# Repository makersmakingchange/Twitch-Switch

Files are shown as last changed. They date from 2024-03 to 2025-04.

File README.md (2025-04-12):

<!---  Open Source Assistive Technology: GitHub Readme Template Version 1.1 (2024-Mar-15)  --->

<!--- INSTRUCTIONS This is a markdown template for creating the README.md file in a GitHub repository. This file is rendered and displayed automatically when someone visits the repository.  --->  
 
 <!---  TITLE Should match the name of the GitHub repository. Choose something descriptive rather than whimsical.   --->
# Twitch Switch

<!---  SUMMARY A brief summary of the project. What it does, who it is for, how much it costs.  --->
The Twitch Switch is for users with limited movement capabilities. Up to three small wireless sensors can capture very small movements. The Twitch Switch can be used for activating up to three switch adapted devices or emulating a mouse or keyboard to operate a digital device such as a computer. 

The Twitch Switch works best for someone who is only able to perform small movements. There are three sensors that can be placed wherever the user has the most controlled, repeatable, intentional movement. Sensor placement can include on the user's finger, wrist, foot, or head. The sensors are powered by rechargeable batteries and connect wirelessly to a controller. The sensitivity of each sensor can be adjusted using knobs on the controller.

The first way to use the Twitch Switch allows the user to activate up to 3 switch adapted devices. Whenever the corresponding switch is moved (even slightly!), the switch adapted device will be activated. 
The second way to use the Twitch Switch is for controlling a digital device such as a computer, tablet, or smartphone. The Twitch Switch can connect via Bluetooth or USB, and has 3 modes: mouse mode, tablet mode, and keyboard mode (which is best for switch control).

The Twitch Switch is intended primarily for people who have some controlled, repeatable, intentional movement, but otherwise have limited mobility and/or dexterity. This device may be beneficial for users with cerebral palsy (CP), spinal cord injuries (SCI), amyotrophic lateral sclerosis (ALS), muscular dystrophy (MD), locked-in syndrome (LIS), traumatic brain injury (TBI), or other disabilities or conditions that significantly limit movement.

The total cost of materials to build this device is around \$360 (plus component shipping). The cost of materials per unit is around \$200 (plus component shipping) if you are able to build in bulk.

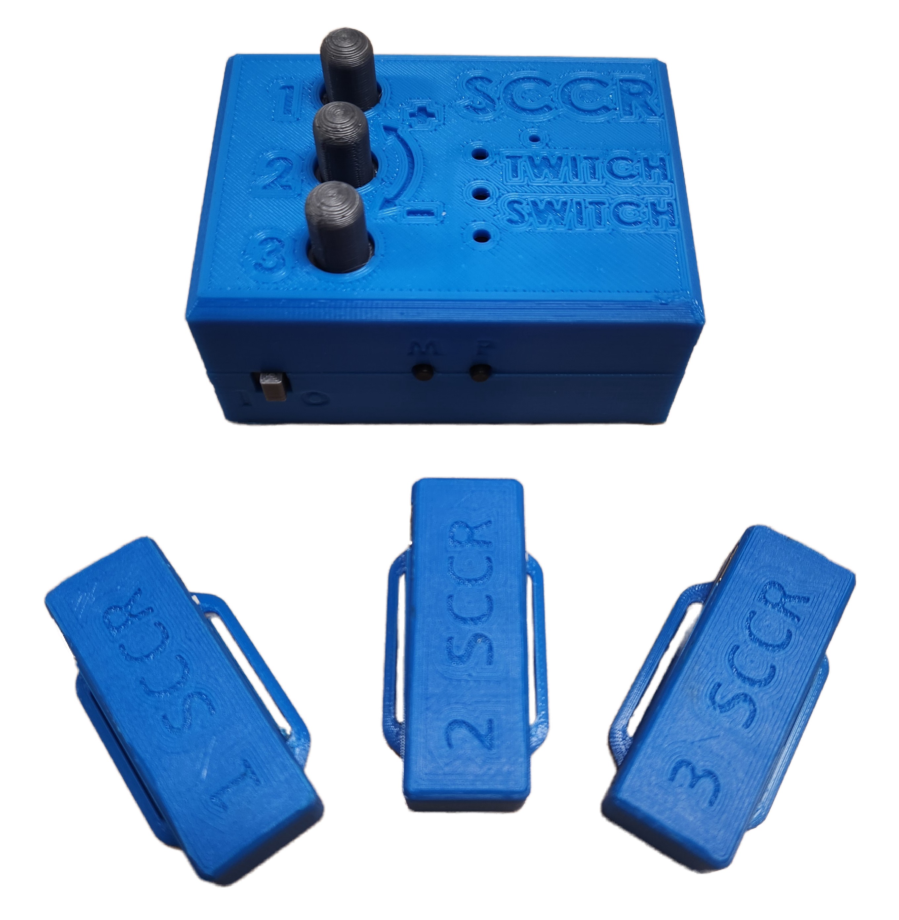
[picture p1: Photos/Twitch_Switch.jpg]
Picture of a Twitch Switch with the controller and three wearable sensors.


## More info at
- [Makers Making Change Assistive Device Library Listing](https://www.makersmakingchange.com/s/product/twitch-switch/01tJR000003UiebYAC)

## How to Obtain the Device
### 1. Do-it-Yourself (DIY) or Do-it-Together (DIT)

This is an open-source assistive technology, so anyone is free to build it. All of the files and instructions required to build the device are contained within this repository. Refer to the Maker Guide below.

### 2. Request a build of this device

You may also submit a build request through the [Makers Making Change Assistive Device Listing](https://www.makersmakingchange.com/s/product/twitch-switch/01tJR000003UiebYAC) to have a volunteer maker build the device. As the requestor, you are responsible for reimbursing the maker for the cost of materials and any shipping.

### 3. Build this device for someone else

If you have the skills and equipment to build this device, and would like to donate your time to create the device for someone who needs it, visit the [MMC Maker Wanted](https://makersmakingchange.com/maker-wanted/) section.

## Build Instructions

### 1. Read through the Maker Guide

The [Maker Guide](/Documentation/Twitch_Switch_Maker_Guide.pdf) contains all the necessary information to build this device, including tool lists, assembly instructions, programming instructions and testing.

### 2. Order the Custom PCBs

This build requires two customs PCBS: one custom PCB for the controller and one custom PCB for each of the three sensors. The sensor PCB has a number of surface mount components and it is recommended to have the PCB fabricator assemble these components on the board.

### 3. Order the Off-The-Shelf Components

The [Bill of Materials](/Documentation/Twitch_Switch_BOM.csv) lists all of the parts and components required to build the device.

### 4. Print the 3D Printable components

All of the files and individual print files can be in the [/Build_Files/3D_Printing_Files](/Build_Files/3D_Printing_Files/) folder. Instructions and settings are provided in the 3D Printing Guide section of the [Maker Guide](/Documentation/Twitch_Switch_Maker_Guide.pdf).

### 5. Assemble the Twitch Switch

Reference the [Maker Guide](/Documentation/Twitch_Switch_Maker_Guide.pdf) for the tools and steps required to build each portion.

## How to improve this Device
As open source assistive technology, you are welcomed and encouraged to improve upon the design. 

## Files
### Documentation
| Document             | Version | Link |
|----------------------|---------|------|
| Maker Guide          | 1.0     | [Twitch Switch_Maker_Guide](/Documentation/Twitch_Switch_Maker_Guide.pdf)     |
| Bill of Materials    | 1.0     | [Twitch Switch_Bill_of_Materials](/Documentation/Twitch_Switch_BOM.csv)     |
| User Guide           | 1.0     | [Twitch Switch_User_Guide](/Documentation/Twitch_Switch_User_Guide.pdf)    |
| Changelog            | 1.0     | [Changelog](CHANGES.txt)     |

### Design Files
<!--- DESIGN FILES Include a copy of the original design files to facilitate easy editing and customization. Consider also including a generic format (e.g., STEP) --->
 - [CAD Files](/Design_Files/CAD_Design_Files)
 - [PCB Files](/Design_Files/PCB_Design_Files)

<!--- BUILD FILES Include a copy of the build files intended for manufacturing. This may include svg files for laser cutting, stl files for 3d printing, Gerber files for custom PCBs, and Arduino files for custom firmware --->
### Build Files
 - [3D Printing Files](/Build_Files/3D_Printing_Files)
 - [PCB Build Files](/Build_Files/PCB_Build_Files)
 - [Firmware Files](/Build_Files/Firmware_Files)

<!--- ATTRIBUTION Provide any necessary attribution for designs or components that are included in the device or as part of the project. --->
## Attribution

The Twitch Switch was designed by the Rehabilitation Engineering Department at Horizon Health's, Stan Cassidy Centre for Rehabilitation (SCCR).  Development was supported through the Government of Canada's Innovation Science and Economic Development [Accessible Technology Program](https://ised-isde.canada.ca/site/accessible-technology-program). The ATP program enabled SCCR to deploy numerous Twitch Switches to users at reduced cost.

The latest design (V3.0) incorporates feedback and suggestions from numerous users, clinicians, and volunteer makers.

The latest design incorporates several commercially available open source hardware components from [Adafruit](https://www.adafruit.com/). The Twitch Switch firmware utilizes the [Arduino](https://www.arduino.cc/) development platform, and a number of libraries developed and shared by the open source community.

<!---
This is the attribution for the template.
--->
The documentation template was created by Makers Making Change / Neil Squire Society and is used under a CC BY-SA 4.0 license. It is available at the following link: [https://github.com/makersmakingchange/OpenAT-Template](https://github.com/makersmakingchange/OpenAT-Template)

<!--- CONTRIBUTORS List the names of the people that contributed to the design. This could include the original source of the idea, designers, testers, documenters, etc. --->
### Contributors
- Rachelle Bernier, Horizon Health Network. 
- Marla Calder, Horizon Health Network 
- Natasha Hanson, Horizon Health Network 
- Dorian Hawkes, Horizon Health Network 
- Rick McCaskill, Horizon Health Network 
- Billie O'Connor, Horizon Health Network 
- Kristen Culberson, Horizon Health Network 
- Josie Versloot, Neil Squire Society / Makers Making Change
 
<!--- LICENSE Add the year(s) for the copyright and the Designer Name. You may use the standard set of open licenses or choose your own for the hardware, software, and accompanying materials. --->
## License
Copyright (c) 2020-2024 Stan Cassidy Center for Rehabilitation.

This repository describes Open Hardware:
 - Everything needed or used to design, make, test, or prepare the Twitch Switch is licensed under the [CERN 2.0 Weakly Reciprocal license (CERN-OHL-W v2) or later](https://cern.ch/cern-ohl ) .
 - All software is under the [GNU General Public License v3.0 (GPL-3.0)](https://www.gnu.org/licenses/gpl.html).
 - Accompanying material such as instruction manuals, videos, and other copyrightable works that are useful but not necessary to design, make, test, or prepare the Twitch Switch are published under a [Creative Commons Attribution-ShareAlike 4.0 license (CC BY-SA 4.0)](https://creativecommons.org/licenses/by-sa/4.0/) .

You may redistribute and modify this documentation and make products using it under the terms of the [CERN-OHL-W v2](https://cern.ch/cern-ohl).
This documentation is distributed WITHOUT ANY EXPRESS OR IMPLIED WARRANTY, INCLUDING OF MERCHANTABILITY, SATISFACTORY QUALITY AND FITNESS FOR A PARTICULAR PURPOSE.
Please see the CERN-OHL-W v2 for applicable conditions.

Source Location: https://github.com/makersmakingchange/Twitch-Switch

List of open source licenses. Hardware: CERN-OHL-W-2.0, Software: GPL-3.0-or-later, Documentation: CC-BY-SA-4.0.

---

<!-- ABOUT MMC START -->
## About Makers Making Change
[Makers Making Change Logo](https://www.makersmakingchange.com/)

Makers Making Change is a program of [Neil Squire](https://www.neilsquire.ca/), a Canadian non-profit that uses technology, knowledge, and passion to empower people with disabilities.

Makers Making Change leverages the capacity of community based Makers, Disability Professionals and Volunteers to develop and deliver affordable Open Source Assistive Technologies.

 - Website: [www.MakersMakingChange.com](https://www.makersmakingchange.com/)
 - GitHub: [makersmakingchange](https://github.com/makersmakingchange)
 - Bluesky: [@makersmakingchange.bsky.social](https://bsky.app/profile/makersmakingchange.bsky.social)
 - Instagram: [@makersmakingchange](https://www.instagram.com/makersmakingchange)
 - Facebook: [makersmakechange](https://www.facebook.com/makersmakechange)
 - LinkedIn: [Neil Squire Society](https://www.linkedin.com/company/neil-squire-society/)
 - Thingiverse: [makersmakingchange](https://www.thingiverse.com/makersmakingchange/about)
 - Printables: [MakersMakingChange](https://www.printables.com/@MakersMakingChange)

### Contact Us
For technical questions, to get involved, or to share your experience we encourage you to [visit our website](https://www.makersmakingchange.com/) or [contact us](https://www.makersmakingchange.com/s/contact).
<!-- ABOUT MMC END -->

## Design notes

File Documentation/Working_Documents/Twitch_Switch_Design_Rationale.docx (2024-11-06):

# Introduction

# Research

## Commercially Available Options

Title
Link
Author
License
Cost
Notes

## DIY Options

Title
Link
Author
License
Cost
Test Build (Y/N)
Add to Library (Y/N)
Notes

## Research Summary

<Summary of findings; potentially viable solutions; any gaps in existing options>

# Requirements

## Goals

G01
G02
G03

## Functional Requirements

F01
F02
F03

## Non-functional Requirement

NF01
NF02
NF03

## Constraints

C01
C02
C03

# Ideation

## Key Features

# Conceptual Design

# Prototyping

# Testing

# Detailed Design

# MVP Design

# Final Design

Programmer

https://github.com/SpenceKonde/AVR-Guidance/blob/master/UPDI/jtag2updi.md

Required Hardware

There has been some debate and questions have been raised over whether the recommendations below are the best. More study is required.

A USB serial adapter These can be had for as low as $1 on eBay and AliExpress based on the CH340G, slightly more for CP210x or "FT232". Ideally, you want to dedicate a serial adapter to this purpose for ease of use, rather than having to connect and disconnect things every time you want to switch between programming with it and using as a serial adapter

a fast signal Schottky diode such as one of the BAT series (BAT43, BAT54) or any of many others (recommended) or a resistor (see below to figure out value)).

1 resistor, a few hundred ohms - 220 to 1k, even 2k is fine (may not be needed).

A few jumper wires. Plan to replace these periodically if you use it a lot. Cheap dupont terminals don't last. Actual DuPont terminals (now made by Amphenol F. C. I) hold up much better, but they cost a fortune.

# Opportunities for Improvement / Future Work

## Controller

- Slide switch is tricky to solder, consider a through hole option
- Radio is a bit tricky to solder
- Could a 3D printed piece work for the LED spacer instead of the tubing? This would then be one less part to buy, and not have to worry about the precision of the cut on the tubing (slightly crooked causes the LED to be crooked)
- Add chamfers to screw holes to make screws easier to insert
- Consider adding a shadow line/inner ledge to help with alignment while screwing the case together
- 5.5 cm seemed to be a bit too wide for the foam, the PCB didn’t quite lay flat, maybe cut this down to 5.3 or 5 cm
- Covers on the buttons on the side could make them easier to press
- Foam pushes up on PCB, and there is nothing to keep the PCB down on the left side, so the knob buttons are getting jammed by being pressed down by the enclosure
- Consider adding bumps to the knobs to make them easier to turn
- Screws
  - 25 mm M2 Screws are hard to source in small quantities. These could be replaced with shorter sheet metal type screws to fasten the enclosure
  - Screws can be easy to strip

## Sensors

- Same as above, slide switch and radio are tricky to solder
- Consider adding hard stops to the sensor enclosure bottom to prevent the PCB from getting pushed down too far and damaging the slide switch
  - I accidentally pushed mine too far down and the slide switch bent upwards
- Consider adding a switch cover to the slide switch on the sensor to make it easier to turn on and off
- Easier way to program boards that does not require custom programmer
- If using custom programmer, more solid connection

## Lithium Batteries

- Need to be extremely cautious with the polarity of connectors from different suppliers!
- These can pose a safety risk and the user should be warned accordingly.

© 2023 by <Author>. This work is licensed under the CC BY SA 4.0 License: http://creativecommons.org/licenses/by-sa/4.0 Files available at <Replace with MMC Library Link> Page 1 of 1

VX.X | <MONTH> <YEAR> <Device Name> Design Rationale

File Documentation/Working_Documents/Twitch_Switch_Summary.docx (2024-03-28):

This document is intended to be a summary of a device to make it easier to add to the website.

# Product Information

## Product Name

Twitch Switch

## Device Category

| Adapted Toys
| Aids for Daily Living (ADL)
X | Assistive Switches
| Communication Aids (AAC)
X | Computer Access
| Environmental Controls
X | Gaming
| Keyguard
| Kits
| LipSyncs
| Mounting
| Recreation and Leisure
| Seating and Positioning
| Switch Interfaces
| Writing Aids

## User Value Statement

An alternative to assistive switches, the Twitch Switch allows you to activate up to 3 switch adapted devices, or emulate a mouse or keyboard with movement as subtle as twitching your eyebrow.

## Designer

Stan Cassidy Centre for Rehabilitation

# Device Info

## Overview

The Twitch Switch is for users with limited movement capabilities. Up to three small wireless sensors can capture very small movements. The Twitch Switch can be used for activating up to three switch adapted devices or emulating a mouse or keyboard to operate a digital device such as a computer.

The Twitch Switch works best for someone who is only able to perform small movements. There are three sensors that can be placed wherever the user has the most controlled, repeatable, intentional movement. Sensor placement can include, but not limited to, on the user’s finger, wrist, foot, or head. The sensors are powered by rechargeable batteries and connect wirelessly to a controller. The sensitivity of each sensor can be adjusted using knobs on the controller.

The first way to use the Twitch Switch allows the user to activate up to 3 switch adapted devices. Whenever the corresponding switch is moved (even slightly!), the switch adapted device will be activated.

The second way to use the Twitch Switch is for controlling a digital device such as a computer, tablet, or smartphone. The Twitch Switch can connect via Bluetooth or USB, and has 3 modes: mouse mode, tablet mode, and keyboard mode (which is best for switch control).

## Disability Type

Select one or more disability types:

X | Agility / Dexterity
| Arthritis
| Cognitive
| Hearing
| Mobility
X | Mobility
| Other
| Pain
X | SCI
| Vision

## Disability Type Description

The Twitch Switch is intended primarily for people who have some controlled, repeatable, intentional movement, but otherwise have limited mobility and/or dexterity. This device may be beneficial for users with cerebral palsy (CP), spinal cord injuries (SCI), amyotrophic lateral sclerosis (ALS), Multiple sclerosis (MS), muscular dystrophy (MD), locked-in syndrome (LIS), traumatic brain injury (TBI), or other disabilities or conditions that significantly limit movement. Although the sensitivity of the wireless sensors can be adjusted to meet the users unique movement, small “twitch” like movements are ideal for optimal functionality of the Twitch Switch.

## How To Use

Below is a brief summary of how to use the Twitch Switch. For more details, as well as accompanying photos, please see the User Guide.

Setup

Start by positioning the sensors where the user has the most controlled, repeatable, intentional movement. Sensor placement can include on the user’s finger, wrist, foot, or head. For more information see the User Guide.

Connecting to Host Device

If you would like to use your Twitch Switch to control a digital device (such as a computer, tablet, or smart phone), you can connect to your host device using Bluetooth or through a wired USB connection. If you would like to use your Twitch Switch to control a switch adapted device, plug in a male to male 3.5 mm cable to both the Twitch Switch Controller and the switch adapted device.

Wireless Connection to Digital Device

To connect via Bluetooth, turn on the sensors, and then turn on the main controller unit, then go to your computer, smart phone, or tablet, and turn on Bluetooth and pair to a new device. Select “Twitch Switch” and pairing will occur.

Wired Connection to Digital Device

To connect via USB, turn on the sensors, then plug in a micro-USB into the Twitch Switch Controller and plug the other end into your host device (some host devices will need an adapter, see the User Guide for more information).

Usage

To use with a switch adapted device, simply activate the corresponding sensor (sensor 1 if plugged into jack 1) to activate the switch adapted device.

To use with a digital device (such as a computer, tablet, or smartphone) there are three different modes: mouse mode, tablet mode, and keyboard mode.

- Mouse mode will move your mouse cursor up and down, left and right, and perform a left click.
- Tablet mode will perform a left click, scroll the page up, and scroll the page down.
- Keyboard mode, which is often used for switch control, will perform keypresses of F1, F2, and F3.

Changing Mode

To change modes between mouse mode, tablet mode, and keyboard mode, simply press the “M” button on the side of the enclosure.

## Estimated Cost

The estimated material cost of the device:

| $0 - $10
| $11 - $25
| $26 - $50
| $51 - $100
X | $101 - $250
| $250+

## Attribution

The Twitch Switch was designed by the Rehabilitation Engineering Department at Horizon Health’s Stan Cassidy’s Centre for Rehabilitation (SCCR). Development was supported through the Government of Canada’s Innovation Science and Economic Development Accessible Technology Program (https://can01.safelinks.protection.outlook.com/?reserved=0) (ATP). The ATP program enabled SCCR to deploy numerous Twitch Switches to users at reduced cost.

The latest design incorporates feedback and suggestions from numerous users, clinicians, and volunteer makers.

The latest design incorporates several commercially available open source hardware components from Adafruit (https://can01.safelinks.protection.outlook.com/?url=https%3A%2F%2Fwww.adafruit.com%2F&reserved=0). The Twitch Switch firmware utilizes the Arduino (https://can01.safelinks.protection.outlook.com/?url=https%3A%2F%2Fwww.arduino.cc%2F&reserved=0) development platform, and a number of libraries developed and shared by the open source community. Full details are available on GitHub (https://can01.safelinks.protection.outlook.com/?reserved=0).

Contributors to this iteration of the Twitch Switch

Designers:

- Rachelle Bernier, Horizon Health Network.
- Marla Calder, Horizon Health Network
- Natasha Hanson, Horizon Health Network
- Dorian Hawkes, Horizon Health Network
- Rick McCaskill, Horizon Health Network
- Billie O’Connor, Horizon Health Network
- Kristen Culberson, Horizon Health Network
- Josie Versloot, Neil Squire Society / Makers Making Change

# Maker Info

## Project Skills

X | 3D Printing
X | Custom PCB
X | Electronics
| Laser Cutting
| Mechanics
X | Software
X | Soldering
| Woodworking
| Other

## Skills Description

This build involves an intermediate level of 3D printing, and an advanced level of soldering, Arduino firmware, and assembly. It also involves ordering two custom PCBs, including a PCB with surface mount components. This build has some surface mount soldering.

## Tools Needed

X | 3D Printer
X | Common Hand Tools
| Common Power Tools
| Laser Cutter
X | Soldering Iron
| Specialized Tooling

## Print time (hrs)

6.0

## Assembly time (hrs)

4.0

## Build Instructions

The Twitch Switch hardware consists of off-the-shelf electronics and hardware components, 3D printed components, and two custom printed circuit boards (PCBs). It is divided into two main parts: the Twitch Switch Controller and the Twitch Switch Sensors. The build has some surface mount components to solder, which is more advanced than through hole soldering. The sensors use a custom programmer to flash the Arduino code to them, which involves creating this programmer with a breadboard and a few components. For more detailed build instructions, see the Maker Guide.

## Download Link

https://github.com/makersmakingchange/Twitch-Switch/archive/refs/heads/main.zip

## Project Link

## https://github.com/makersmakingchange/Twitch-Switch

# License

## License

Copyright (c) 2024 Stan Cassidy Centre for Rehabilitation.

This repository describes Open Hardware:

- Everything needed or used to design, make, test, or prepare the Twitch Switch is licensed under the CERN 2.0 Weakly Reciprocal license (CERN-OHL-W v2) or later (https://cern.ch/cern-ohl) .
- All software is under the GNU General Public License v3.0 (GPL-3.0) (https://www.gnu.org/licenses/gpl.html).
- Accompanying material such as instruction manuals, videos, and other copyrightable works that are useful but not necessary to design, make, test, or prepare the Twitch Switch are published under a Creative Commons Attribution-ShareAlike 4.0 license (CC BY-SA 4.0) (https://creativecommons.org/licenses/by-sa/4.0/) .

You may redistribute and modify this documentation and make products using it under the terms of the CERN-OHL-W v2 (https://cern.ch/cern-ohl). This documentation is distributed WITHOUT ANY EXPRESS OR IMPLIED WARRANTY, INCLUDING OF MERCHANTABILITY, SATISFACTORY QUALITY AND FITNESS FOR A PARTICULAR PURPOSE. Please see the CERN-OHL-W v2 for applicable conditions.

Source Location: https://github.com/makersmakingchange/Twitch-Switch

© 2024 by Neil Squire Society. This work is licensed under the CC BY SA 4.0 License: http://creativecommons.org/licenses/by-sa/4.0 Page 1 of 2

V3.0 | MARCH 2024 Twitch Switch Summary

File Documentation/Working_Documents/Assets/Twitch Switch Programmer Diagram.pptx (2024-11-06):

## Twitch Switch Programmer Diagram

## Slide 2

Solderless Breadboard

| a | b | c | d | e
2 | | TXD
3
4 | | RXD | | | Mid
5 | | GND | | | GND

CP2102 Programmer

Twitch Switch Sensor PCB

3V3

TXD

. Diode

VCC

RXD

+

GND

GND

5V

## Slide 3

Solderless Breadboard

| a | b | c | d | e
2 | | TXD
3
4 | | RXD
5 | | GND

CP2102 Programmer

3V3

TXD

. Diode

RXD

+

GND

5V

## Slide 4

Solderless Breadboard

| a | b | c | d | e
2 | | TXD
3
4 | | RXD
5 | | GND

CP2102 Programmer

3V3

TXD

RXD

GND

5V

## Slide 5

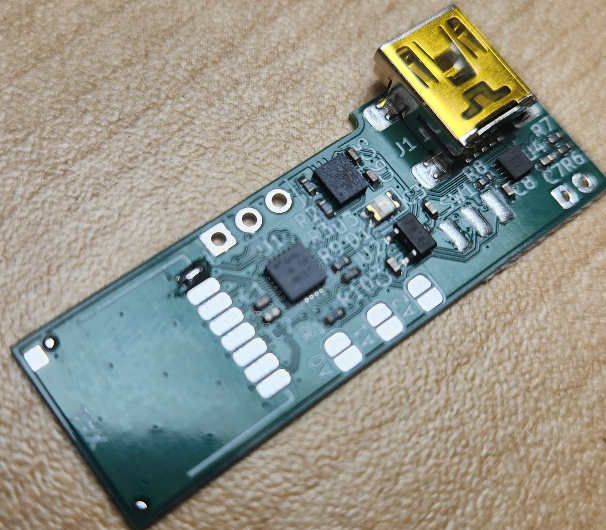
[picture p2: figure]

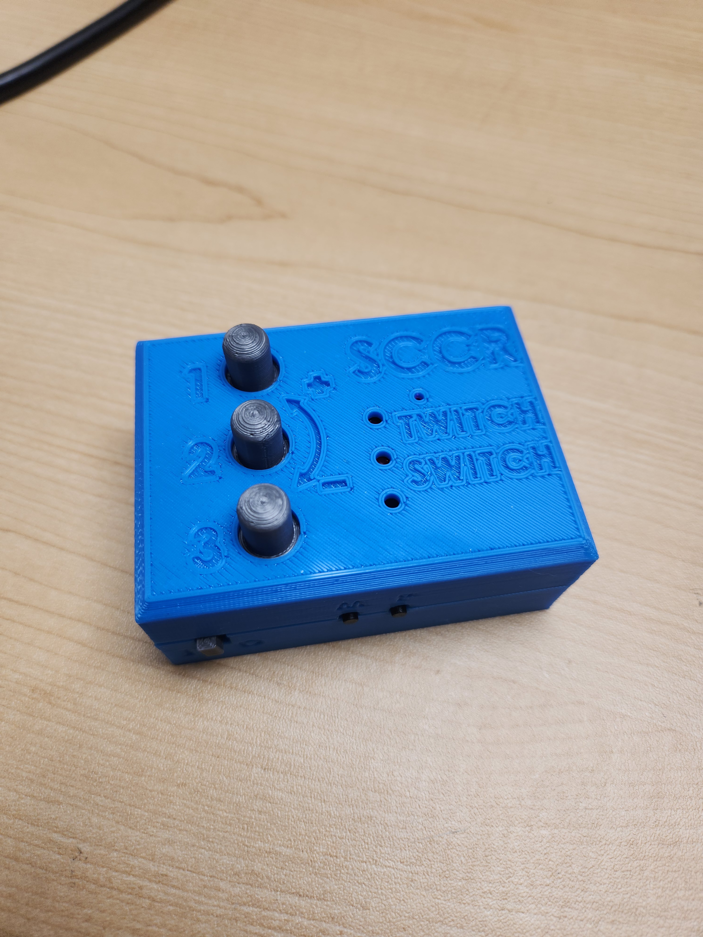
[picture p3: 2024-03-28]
Photos/Twitch_Switch1.jpg

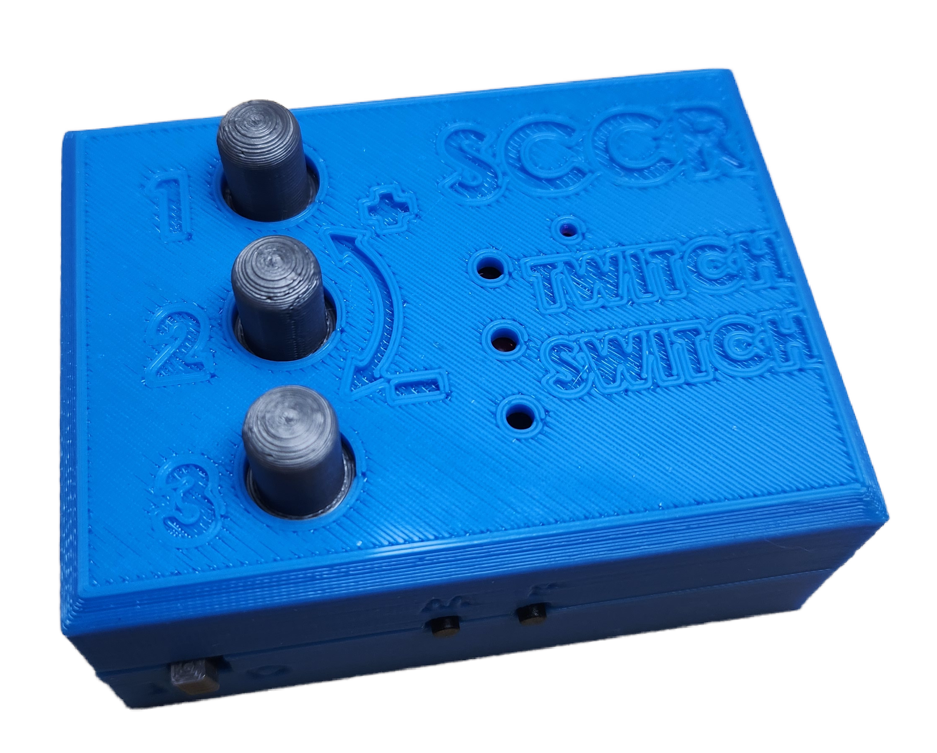
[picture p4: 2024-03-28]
Photos/Twitch_Switch1-NoBackground.png

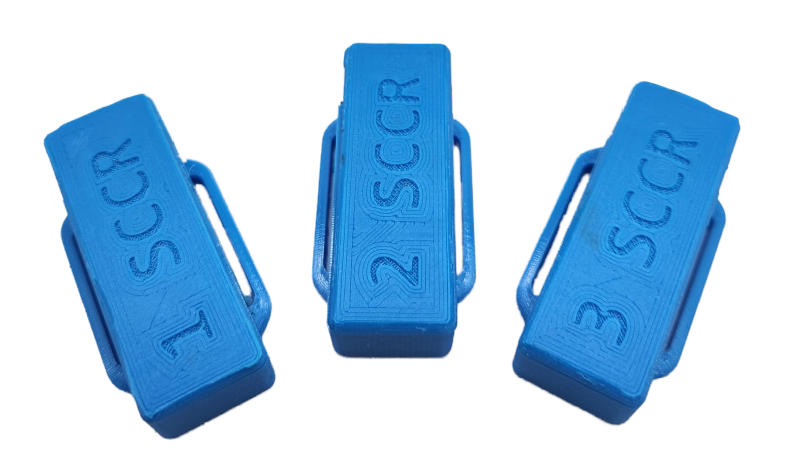
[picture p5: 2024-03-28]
Photos/Twitch_Switch_Sensors_NoBackground.png

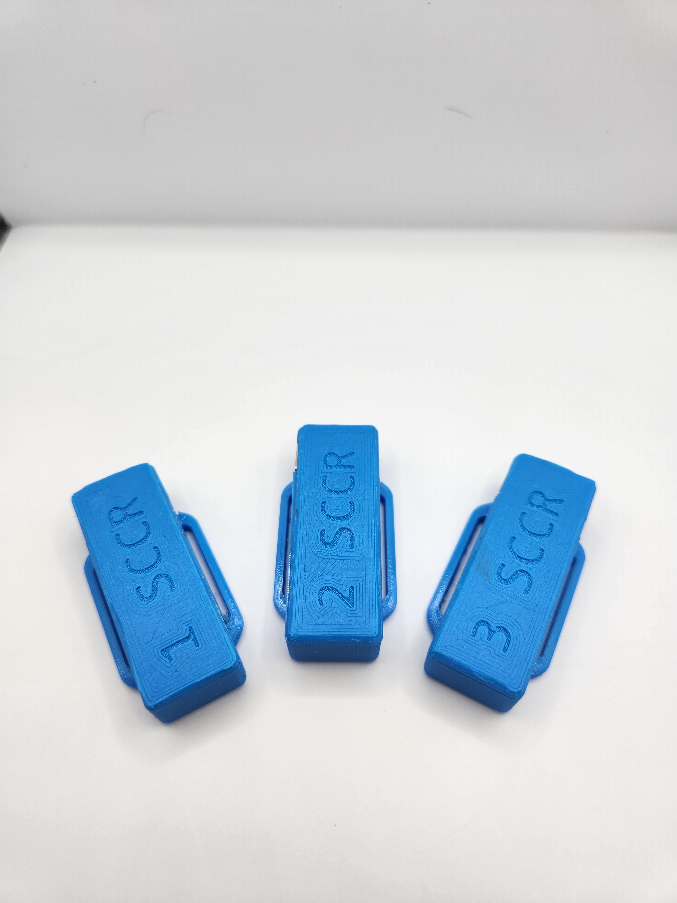
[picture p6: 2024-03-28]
Photos/Twitch_Switch_Sensors.jpg

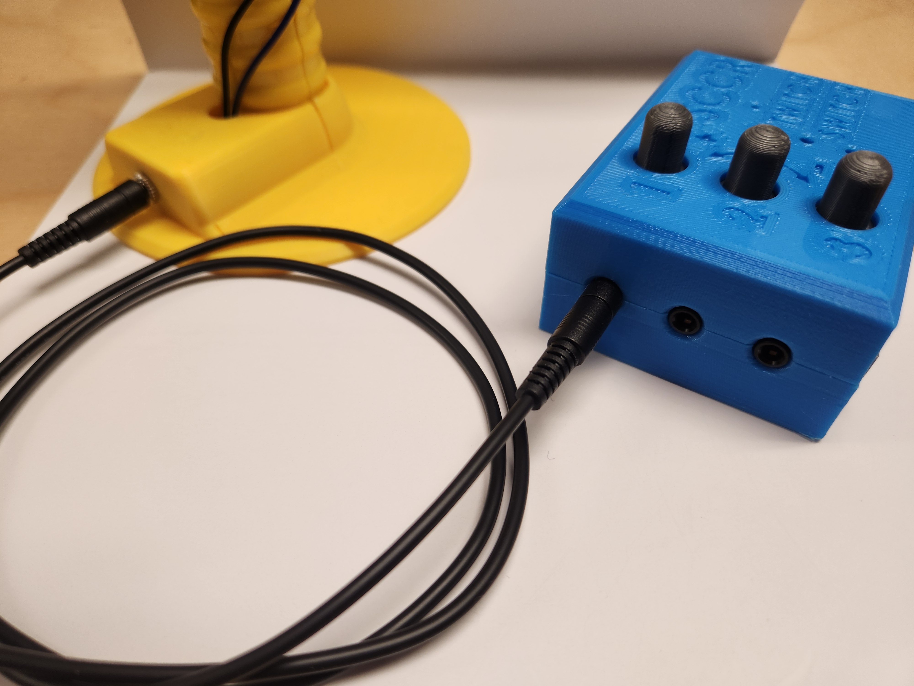
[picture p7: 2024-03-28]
Photos/Twitch_Switch_Toy_Closeup.jpg

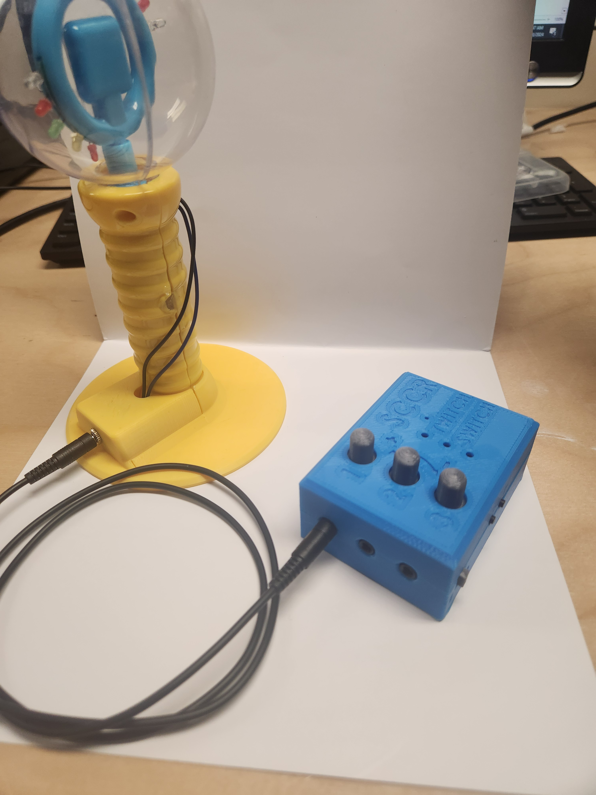
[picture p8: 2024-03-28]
Photos/Twitch_Switch_Toy.jpg

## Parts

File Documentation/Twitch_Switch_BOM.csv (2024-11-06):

 | Twitch Switch |  |  |  |  |  |  |  | Total filament (g) |  |  | Unit Cost | Total Cost | Total Print time (hr)
 | Version: | 3.1 |  | Last updated: | 2024-Mar-25 |  |  |  | 56 |  |  | $197.29 | $373.07 | 6:14
ID | Part | Description |  | Manufacturer | MPN | Supplier | Supplier PN | QTY | QTY / PKG | PKGs | $/PKG | Price per Unit | Total Price |  | Link | Alternate | Notes
 | Electronics
Twitch Controller |  |  |  |  |  |  |  | 1
A04 | J1, J2, J3 | CONN JACK STEREO 3.5MM TH R/A |  | Kycon, Inc. | STX-3000 | Digi-Key | 2092-STX-3000-ND | 3 | 1 | 3 | $1.18 | $3.54 | $3.54 |  | https://www.digikey.ca/en/products/detail/kycon-inc/STX-3000/9975995
A05 | U1, U2, U3 | DIP-4 400V/120 MA, SSR RELAY SPS |  | Bright Toward Industrial Co., Ltd. | AB30 | Digi-Key | 3008-AB30-ND | 3 | 1 | 3 | $2.72 | $8.16 | $8.16 |  | https://www.digikey.ca/en/products/detail/bright-toward-industrial-co-ltd/AB30/13556959
A09 | R1, R2, R3 | RES 680 OHM 5% 1/4W AXIAL |  | YAGEO | CFR-25JB-52-680R | Digi-Key | 680QBK-ND | 3 | 1 | 3 | $0.16 | $0.48 | $0.48 |  | https://www.digikey.ca/en/products/detail/yageo/CFR-25JB-52-680R/2826
A06 | R4, R5, R6 | RES 330 OHM 5% 1/4W AXIAL |  | YAGEO | CFR-25JB-52-330R | Digi-Key | 330QBK-ND | 3 | 1 | 3 | $0.16 | $0.48 | $0.48 |  | https://www.digikey.ca/en/products/detail/yageo/CFR-25JB-52-330R/1636
A12 | SW2, SW3 | 6 X 7.4 MM, 15.3 MM ACTUATOR HEI |  | CUI Devices | TS11-674-153-BK-260-RA-D | Digi-Key | 2223-TS11-674-153-BK-260-RA-D-ND | 2 | 1 | 2 | $0.24 | $0.48 | $0.48 |  | https://www.digikey.ca/en/products/detail/cui-devices/TS11-674-153-BK-260-RA-D/16562823
A03 | SW1 | SWITCH SLIDE SPDT 100MA 12V |  | Nidec Copal Electronics | CSS-1210TB | Digi-Key | CSS-1210TB | 1 | 1 | 1 | $0.91 | $0.91 | $0.91 |  | https://www.digikey.ca/en/products/detail/nidec-components-corporation/CSS-1210TB/1124209
A02 | XA1 | ADAFRUIT FEATHER NRF52840 EXPRES |  | Adafruit Industries LLC | 4062 | Digi-Key | 1528-2828-ND | 1 | 1 | 1 | $39.10 | $39.10 | $39.10 |  | https://www.digikey.ca/en/products/detail/adafruit-industries-llc/4062/9843410
A07 | SW4, SW5, SW6 | ROTARY ENCODER MECHANICAL 24PPR |  | Bourns Inc. | PEC12R-4230F-S0024 | Digi-Key | PEC12R-4230F-S0024-ND | 3 | 1 | 3 | $2.49 | $7.47 | $7.47 |  | https://www.digikey.ca/en/products/detail/bourns-inc/PEC12R-4230F-S0024/4699285
A10 | TUBE | Silicon tubing 3 mm ID 5 mm OD x 8 mm long |  | QJZXUEZHEN |  | Amazon |  | 24 | 1000 | 1 | $9.30 | $0.22 | $9.30 |  | https://a.co/d/d2qAuZv
A11 | D1, D2, D3 | LED RED DIFFUSED T/H |  | Lite-On Inc. | LTL2R3KRD-EM | Digi-Key | 160-1853-ND | 3 | 1 | 3 | $0.52 | $1.56 | $1.56 |  | https://www.digikey.ca/en/products/detail/liteon/LTL2R3KRD-EM/2675133
A08 | XA2 | Radio nRF24L01P 2.4 GHz Wireless Module |  | CANADUINO | nRF24L01-Mini | Amazon |  | 1 | 2 | 1 | $5.50 | $2.75 | $5.50 |  | https://www.amazon.ca/gp/product/B07F1PXPXX/ref=ppx_yo_dt_b_search_asin_title?ie=UTF8&psc=1 |  | 4 total: 1 for controller, 3 for sensors
A14 |  | 12- and 16 pin female headers |  | Adafruit Industriess LLC | 2886 | Digi-Key | 1528-1560-ND | 1 | 1 | 1 | $1.36 | $1.36 | $1.36 |  | https://www.digikey.ca/en/products/detail/adafruit-industries-llc/2886/5823440
A15 | BAT1 | 3.7V 2000mAh lithium-ion polymer battery |  | Canada Robotix | 2-03-01-02-06 | Canada Robotix | 2528 | 1 | 1 | 1 | $14.99 | $14.99 | $14.99 |  | https://www.canadarobotix.com/products/2528
A19 | SHT | 65 mm x 50 mm x 3 mm insulating foam |  | Kiera Grace Store |  | Amazon |  | 1 | 192 | 1 | $8.99 | $0.05 | $8.99 |  | https://www.amazon.ca/Time-Crafts-sheet-inches-Peach/dp/B0764QHCQS | See below
A20 |  | M2x0.4 x 5 mm screws, flat head |  | B&F Fastener Supply | MPMS 002 0005 PH | Digi-Key | H738-ND | 2 | 100 | 1 | 26.33 | $0.53 | $26.33 |  | https://www.digikey.ca/en/products/detail/b-f-fastener-supply/MPMS-002-0005-PH/274949
A21 |  | M2x0.4 x 25 mm screws, flat head |  | McMaster Carr | 92010A111 | McMaster Carr | 92010A111 | 4 | 50 | 1 | $9.31 | $0.74 | $9.31 |  | https://www.mcmaster.com/catalog/130/3484/92010A111
Twitch Sensors |  |  |  |  |  |  |  | 3
C04 | J3 | CONN HEADER R/A 2POS 2MM |  | JST Sales America Inc. | S2B-PH-K-S(LF)(SN) | Digi-Key | 455-1719-ND | 3 | 1 | 3 | $0.25 | $0.75 | $0.75 |  | https://www.digikey.ca/en/products/detail/jst-sales-america-inc/S2B-PH-K-S/926626
C02 | XA1 | Radio nRF24L01P 2.4 GHz Wireless Module |  | CANADUINO | nRF24L01-Mini | Amazon |  | 3 | 2 | 2 | $5.50 | $8.25 | $11.00 |  | https://www.amazon.ca/gp/product/B07F1PXPXX/ref=ppx_yo_dt_b_search_asin_title?ie=UTF8&psc=1 |  | Combine with above
A15 | BAT2 | 3.7V 110 mAh lithium-ion polymer battery |  | Canada Robotix | 930 | Canada Robotix |  | 3 | 1 | 3 | $5.99 | $17.97 | $17.97 |  | https://www.canadarobotix.com/products/939
Twitch Switch Data / Charging Cables
 | USB-Mini | CBL USB2.0 A PLG-MIN B PLG 3.28' |  | Assmann WSW Components | AK672M/2-1 | Digi-Key | AE1450-ND | 1 | 1 | 1 | $3.57 | $3.57 | $3.57 |  | https://www.digikey.ca/en/products/detail/assmann-wsw-components/AK672M-2-1/930235
 | USB-Micro | USB AM TO USB MICRO, USB 2.0 - 1 |  | Cvilux USA | DH-20M50055 | Digi-Key | 2987-DH-20M50055-ND | 1 | 1 | 1 | $2.24 | $2.24 | $2.24 |  | https://www.digikey.ca/en/products/detail/cvilux-usa/DH-20M50055/13175849
Twitch Switch Adapted Device Cables
 | CBL | 3.5 mm Male-Male Mono Cable |  | Switchcraft Inc. | 33HR07233X | Digi-Key | SC1812-ND | 3 | 1 | 1 | $12.11 | $36.33 | $12.11 |  | https://www.digikey.ca/en/products/detail/switchcraft-inc/33HR07233X/1289530
Twitch Sensor Programmer
D01 |  | CP2102 Programmer |  | Generic |  | Amazon |  | 1 | 2 | 1 | $9.98 | $4.99 | $9.98 |  | https://www.amazon.ca/gp/product/B07D6LLX19
D02 |  | IN4002 Diode |  | Diotec Semiconductor | 1N4002 | Digi-Key | 4878-1N4002CT-ND | 1 | 1 | 1 | $0.15 | $0.15 | $0.15 |  | https://www.digikey.ca/en/products/detail/diotec-semiconductor/1N4002/13164611
D04 |  | Solderless Breadboard |  | DFRobot | FIT0096 | Digi-Key | 1738-1326-ND | 1 | 1 | 1 | $4.43 | $4.43 | $4.43 |  | https://www.digikey.ca/en/products/detail/dfrobot/FIT0096/7597069
D05 |  | Female-to-male Dupont Wire |  | Adafruit Industries LLC | 1953 | Digi-Key | 1528-2233-ND | 5 | 20 | 1 | $2.79 | $0.70 | $2.79 |  | https://www.digikey.ca/en/products/detail/adafruit-industries-llc/1953/7241478?s=N4IgTCBcDaIIYBM4DMBOBXAlgFwAQEYBOAVgGYQBdAXyA
D06 |  | Male-to-Male Dupont Wire |  | Adafruit Industries LLC | 1956 | Digi-Key | 1528-1966-ND | 2 | 20 | 1 | $2.79 | $0.28 | $2.79 |  | https://www.digikey.ca/en/products/detail/adafruit-industries-llc/1956/6827089
 | Custom PCB
 | Part | Description |  | Manufacturer |  | Supplier | Supplier PN | QTY | QTY / PKG | PKG | $/PKG | Price per Unit | Total Price |  | Link
A01 | PCB1 | Twitch Switch Controller Custom PCB |  | JLCPCB |  |  |  | 1 | 5 | 1 | 5 | 1 | 5
C01 | PCB2 | Twitch Switch Sensor Custom PCB |  | JLCPCB |  |  |  | 3 | 15 | 1 | 12.06 | 2.41 | 12.06
C01.1 | PCB2A | Twitch Switch Sensor Custom PCB Assembly |  | JLCPCB |  |  |  | 3 | 15 | 1 | 123.58 | 24.72 | 123.58
 | PCB Shipping | PCB Shipping - DHL Express | Shipping |  |  |  |  | 1 | 5 | 1 | 25 | 5 | 25 |  |  | Kr
 | PCB Shipping | PCB Shipping - Fedex International | Shipping |  |  |  |  | 0 | 5 | 0 | 25 | 0 | 0
 | 3D Printed Parts ESTIMATED PRICING USING 1KG ROLL COST: | $30.00
 | Part | Description |  |  |  |  |  | QTY | Mass (g) |  | Estimated Price | Estimated Price | Estimated Price | Print Time (hr:Min) | Link
A16.1 |  | Twitch Switch Controller Case Top |  |  |  |  |  | 1 | 20 |  | $0.60 | $0.60 | $0.60 | 2:11
A16.2 |  | Twitch Switch Controller Case Bottom |  |  |  |  |  | 1 | 20 |  | $0.60 | $0.60 | $0.60 | 2:13
A17 |  | Switch Cover |  |  |  |  |  | 1 | 1 |  | $0.03 | $0.03 | $0.03 | 0:05
A18 |  | Dial Cover |  |  |  |  |  | 3 | 1 |  | $0.03 | $0.03 | $0.03 | 0:14
C06 |  | Sensor Enclosure Bottom |  |  |  |  |  | 3 | 5 |  | $0.15 | $0.15 | $0.15 | 0:34
C07 |  | Sensor 1 Enclosure Top |  |  |  |  |  | 1 | 3 |  | $0.09 | $0.09 | $0.09 | 0:19
C08 |  | Sensor 2 Enclosure Top |  |  |  |  |  | 1 | 3 |  | $0.09 | $0.09 | $0.09 | 0:19
C09 |  | Sensor 3 Enclosure Top |  |  |  |  |  | 1 | 3 |  | $0.09 | $0.09 | $0.09 | 0:19
 |  |  |  |  |  |  |  |  |  |  | $- | $- | $-
 | Alternatives
 | Part | Description |  | Manufacturer |  | Supplier
 |  | Solderless Breadboard |  | Adafruit Industries LLC | 4539 | Adafruit | 4539 | 1 | 1 | 1 | $5.00 | $5.00 | $5.00 |  | https://www.adafruit.com/product/4539
 |  | Solderless breadbooard |  | Adafruit Industries LLC | 4539 | Digi-Key | 1528-4539-ND | 1 | 1 | 1 | $7.63 | $7.63 | $7.63 |  | https://www.digikey.ca/en/products/detail/adafruit-industries-llc/4539/12082396?s=N4IgTCBcDaIIYBM4DMBOBXAlgFwAQBYBWAZgE4QBdAXyA
 |  | 3.7V 2000mAh lithium-ion polymer battery |  | Adafruit Industries LLC | 2011 | Adafruit | 2011 | 1 | 1 | 1 | $12.50 | $12.50 | $12.50 |  | https://www.adafruit.com/product/2011
A20 |  | M2x0.4 x 5 mm screws |  |  |  | McMaster-Carr | 92010A002 | 2 | 50 | 1 | $12.50 | $0.50 | $12.50
A21 |  | M2x0.4 x 25 mm screws |  |  |  | McMaster-Carr | 92010A111 | 4 | 50 | 1 | $12.50 | $1.00 | $12.50 |  | https://www.mcmaster.com/catalog/130/3484/92010A111
 | CBL | 3.5 mm Male-Male Mono Cable |  | Switchcraft Inc. | 33HR07233X | Digi-Key | SC1812-ND | 3 | 1 | 1 | $12.11 | $36.33 | $12.11 |  | https://www.digikey.ca/en/products/detail/switchcraft-inc/33HR07233X/1289530
 | CBL | Mono Audio Plug Jack Connector Male to Male Cable (3FT) |  |  |  | Amazon.ca |  | 3 | 1 | 1 | $9.95 | $29.85 | $9.95 |  | https://www.amazon.ca/TENINYU-3-5mm-Mono-Cable-Extension/dp/B07PMZXL3Y
 | CBL | 3.5 mm Male-Male Mono Cable |  |  |  | Dollar Store |  | 3 | 1 | 1 | $5.00 | $15.00 | $5.00 |  |  | Stereo cable should work fine
 | SHT | 65 mm x 50 mm x 3 mm insulating foam |  |  |  | Dollar Store |  | 3 | 1 | 1 | $1.00 | $3.00 | $1.00
 |  |  |  |  |  |  |  |  |  |  | $- | $- | $-
 | Twitch Switch PCB Assembly Components (Only required if doing manual surface mount soldering) |  |  |  |  |  |  | 1
 | Part | Description |  | Manufacturer |  | Supplier
C01.2 | J1 | USB C REC GF RA 6P SMT & SMT SHE |  | GCT | USB4135-GF-A | Digi-Key | 2073-USB4135-GF-ACT-ND | 1 | 1 | 1 | $1.12 | $1.12 | $1.12 |  | https://www.digikey.ca/en/products/detail/gct/USB4135-GF-A/16036137
C01.3 | U4 | IC BATT CHG LI-ION 1CELL 10SON |  | Texas Instruments | BQ24045DSQR | Digi-Key | 296-39905-1-ND | 3 | 1 | 3 | $2.68 | $8.04 | $8.04 |  | https://www.digikey.ca/en/products/detail/texas-instruments/BQ24045DSQR/3926683
C01.4 | U1 | IC MCU 8BIT 16KB FLASH 20VQFN |  | Microchip Technology | ATTINY1606-MNR | Digi-Key | 150-ATTINY1606-MNRCT-ND | 3 | 1 | 3 | $1.46 | $4.38 | $4.38 |  | https://www.digikey.ca/en/products/detail/microchip-technology/ATTINY1606-MNR/11476188
C01.5 | U3 | IMU ACCEL/GYRO I2C/SPI 14LGA |  | STMicroelectronics | LSM6DSMTR | Digi-Key | 497-16696-1-ND | 3 | 1 | 3 | $7.32 | $21.96 | $21.96 |  | https://www.digikey.ca/en/products/detail/diodes-incorporated/AP2138N-3-0TRG1/4770631
C01.6 | U2 | IC REG LINEAR 3V 250MA SOT23-3 |  | Diodes Incorporated | AP2138N-3.0TRG1 | Digi-Key | AP2138N-3.0TRG1DICT-ND | 3 | 1 | 3 | $0.60 | $1.80 | $1.80 |  | https://www.digikey.ca/en/products/detail/diodes-incorporated/AP2138N-3-0TRG1/4770631
C01.7 | SW1 | SWITCH SLIDE SPDT 100MA 12V |  | Nidec Copal Electronics | CSS-1210TB | Digi-Key | 563-1091-1-ND | 3 | 1 | 3 | $0.91 | $2.73 | $2.73 |  | https://www.digikey.ca/en/products/detail/nidec-components-corporation/CSS-1210TB/1124209
C01.8 | C1, C5, C6 | CAP CER 0.1UF 25V X5R 0402 |  | Samsung Electro-Mechanics | CL05A104KA5NNNC | Digi-Key | 1276-1043-1-ND | 9 | 1 | 9 | $0.15 | $1.35 | $1.35 |  | https://www.digikey.ca/en/products/detail/samsung-electro-mechanics/CL05A104KA5NNNC/3886701
C01.9 | C2, C3, C4, C7, C8 | CAP CER 1UF 10V X5R 0402 |  | Walsin Technology Corporation | 0402X105K100CT | Digi-Key | 1292-0402X105K100CT-ND | 15 | 1 | 15 | $0.15 | $2.25 | $2.25 |  | https://www.digikey.ca/en/products/detail/walsin-technology-corporation/0402X105K100CT/6707544
C01.10 | D1 | LED RED CLEAR CHIP SMD |  | Kingbright | APT2012EC | Digi-Key | 754-1128-1-ND | 3 | 1 | 3 | $0.47 | $1.41 | $1.41 |  | https://www.digikey.ca/en/products/detail/kingbright/APT2012EC/1747527
C01.11 | R8 | RES 10K OHM 5% 1/16W 0402 |  | Stackpole Electronics Inc | RMCF0402JT10K0 | Digi-Key | RMCF0402JT10K0CT-ND | 3 | 1 | 3 | $0.16 | $0.48 | $0.48 |  | https://www.digikey.ca/en/products/detail/stackpole-electronics-inc/RMCF0402JT10K0/1758206
C01.12 | R1 | RES 100 OHM 5% 1/16W 0402 |  | Stackpole Electronics Inc | RMCF0402JT100R | Digi-Key | RMCF0402JT100RCT-ND | 3 | 1 | 3 | $0.16 | $0.48 | $0.48 |  | https://www.digikey.ca/en/products/detail/walsin-technology-corporation/0402X105K100CT/6707544
C01.13 | R2, R3 | RES 20K OHM 5% 1/16W 0402 |  | Stackpole Electronics Inc | RMCF0402JT20K0 | Digi-Key | RMCF0402JT20K0CT-ND | 6 | 1 | 6 | $0.16 | $0.96 | $0.96 |  | https://www.digikey.ca/en/products/detail/stackpole-electronics-inc/RMCF0402JT20K0/1758166
C01.14 | R7 | RES 2K OHM 5% 1/16W 0402 |  | Stackpole Electronics Inc | RMCF0402JT2K00 | Digi-Key | RMCF0402JT2K00CT-ND | 3 | 1 | 3 | $0.16 | $0.48 | $0.48 |  | https://www.digikey.ca/en/products/detail/stackpole-electronics-inc/RMCF0402JT2K00/1758132
C01.15 | R6 | RES 5.6K OHM 1% 1/16W 0402 |  | Stackpole Electronics Inc | RMCF0402FT5K60 | Digi-Key | RMCF0402FT5K60CT-ND | 3 | 1 | 3 | $0.16 | $0.48 | $0.48 |  | https://www.digikey.ca/en/products/detail/stackpole-electronics-inc/RMCF0402FT5K60/4440018
C01.16 | R9 | RES 215K OHM 1% 1/16W 0402 |  | Stackpole Electronics Inc | RMCF0402FT215K | Digi-Key | RMCF0402FT215KCT-ND | 3 | 1 | 3 | $0.16 | $0.48 | $0.48 |  | https://www.digikey.ca/en/products/detail/stackpole-electronics-inc/RMCF0402FT215K/1761448
C01.17 | R10 | RES 113K OHM 1% 1/16W 0402 |  | Stackpole Electronics Inc | RMCF0402FT113K | Digi-Key | RMCF0402FT113KCT-ND | 3 | 5 | 1 | $0.16 | $0.10 | $0.16 |  | https://www.digikey.ca/en/products/detail/stackpole-electronics-inc/RMCF0402FT113K/1761462
C01.18 | R4, R5 | RES 5.1K OHM 5% 1/16W 0402 |  | Stackpole Electronics Inc | RMCF0402JT5K10 | Digi-Key | RMCF0402JT5K10CT-ND | 6 | 1 | 6 | $0.16 | $0.96 | $0.96 |  | https://www.digikey.ca/en/products/detail/stackpole-electronics-inc/RMCF0402JT5K10/1758112

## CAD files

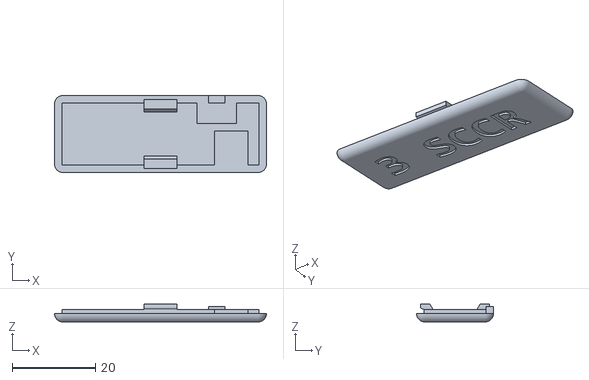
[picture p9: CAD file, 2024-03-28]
Build_Files/3D_Printing_Files/Twitch_Switch_Sensor3_Top_v3.stl
51.0 x 18.5 x 4.30

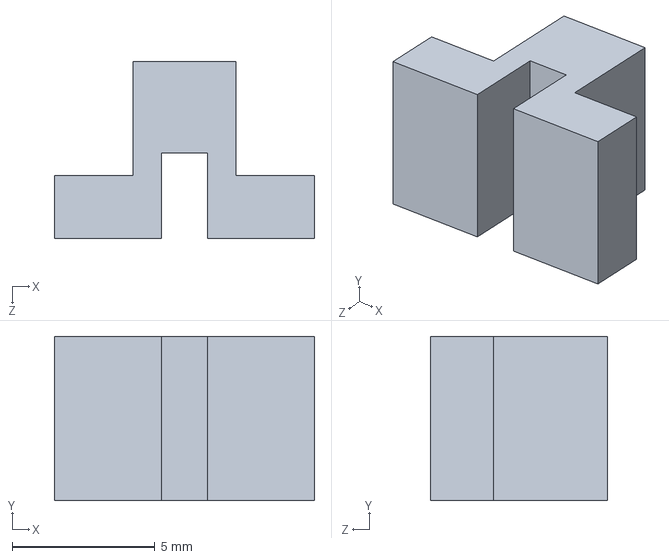
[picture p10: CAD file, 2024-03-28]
Design_Files/CAD_Design_Files/SolidWorks/Twitch_Switch_Controller_Power_Switch_V3.SLDPRT
9.10 x 5.75 x 6.20 mm

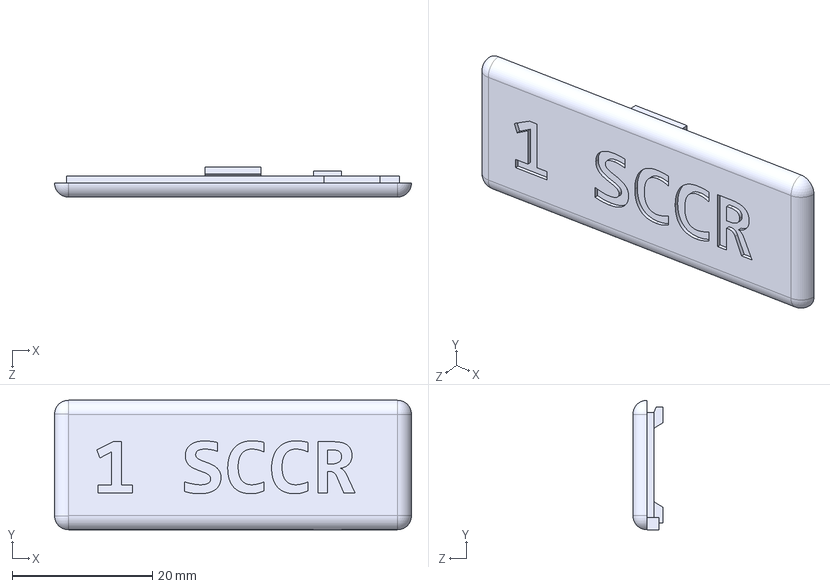
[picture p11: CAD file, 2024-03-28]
Design_Files/CAD_Design_Files/Step/Twitch_Switch_Sensor1_Lid.STEP
51.0 x 18.5 x 4.30 mm

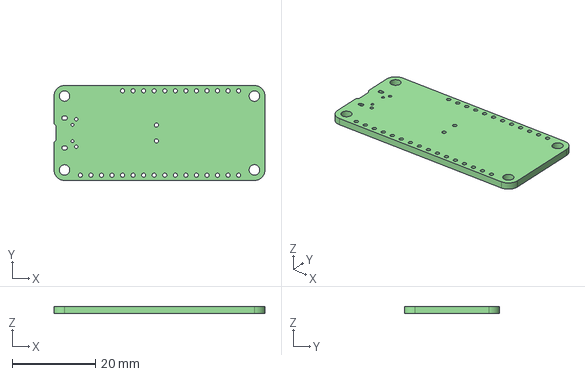
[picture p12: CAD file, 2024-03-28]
Design_Files/PCB_Design_Files/Twitch Switch Base KiCad/3d models/Adafruit nRF52840 Bluefruit Feather Express Rev D.step
50.8 x 22.9 x 1.60 mm

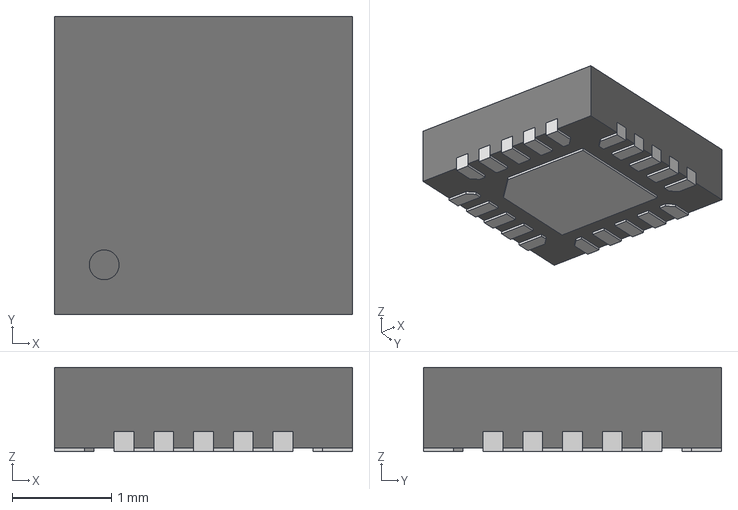
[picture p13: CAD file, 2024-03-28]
Design_Files/PCB_Design_Files/Twitch Switch KiCad/3d-models/VQFN-20-3x3mm.step
3.00 x 3.00 x 0.85 mm
Pads
Main Body

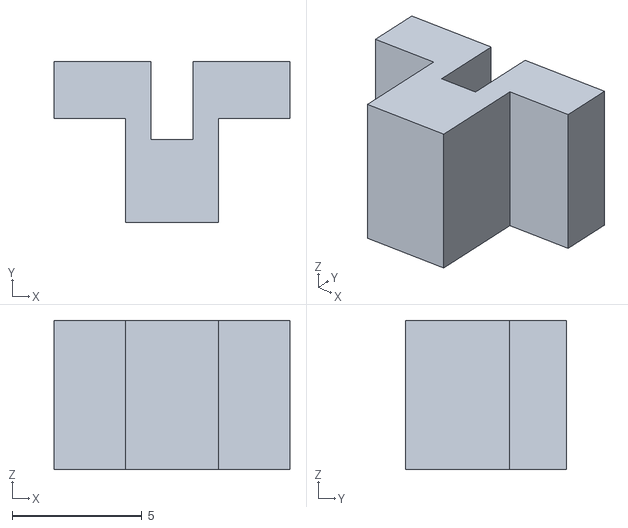
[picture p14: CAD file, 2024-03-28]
Build_Files/3D_Printing_Files/Twitch_Switch_Controller_Power_Switch_v3.STL
9.10 x 6.20 x 5.75

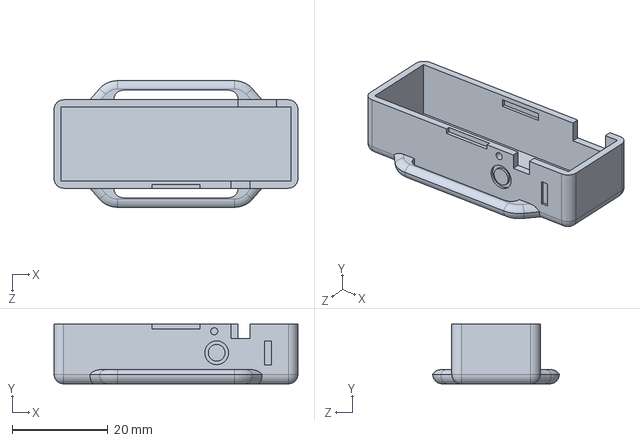
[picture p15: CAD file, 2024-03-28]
Design_Files/CAD_Design_Files/SolidWorks/Twitch_Switch_Sensor_Bottom.SLDPRT
51.0 x 12.5 x 26.5 mm

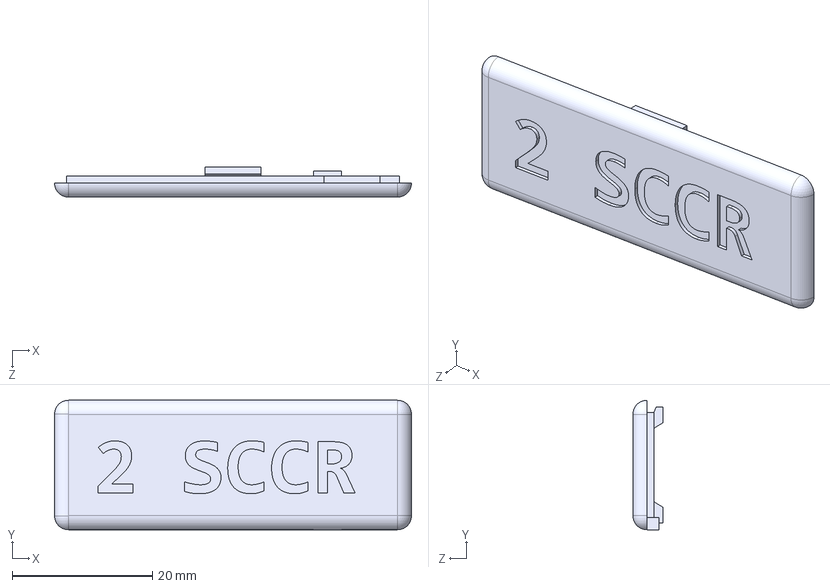
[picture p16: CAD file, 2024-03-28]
Design_Files/CAD_Design_Files/Step/Twitch_Switch_Sensor2_Lid.STEP
51.0 x 18.5 x 4.30 mm

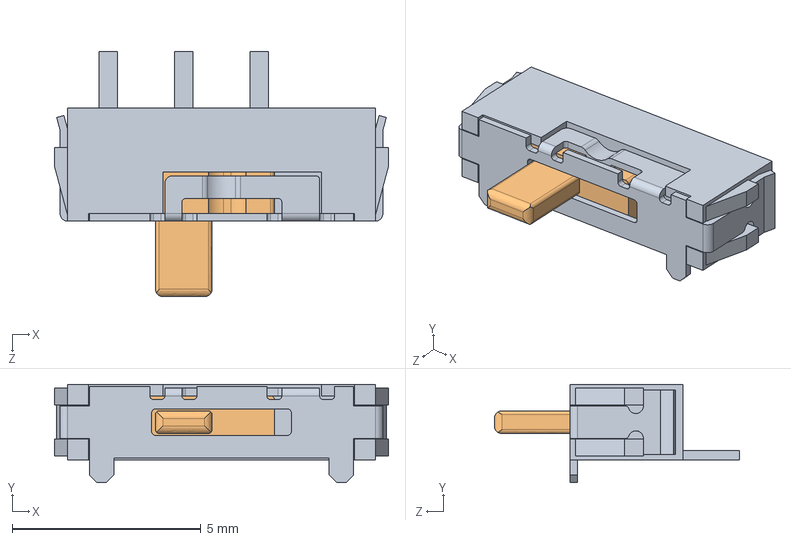
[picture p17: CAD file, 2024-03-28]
Design_Files/PCB_Design_Files/Twitch Switch Base KiCad/3d models/CSS-1210TB.STEP
8.85 x 2.60 x 6.50 mm

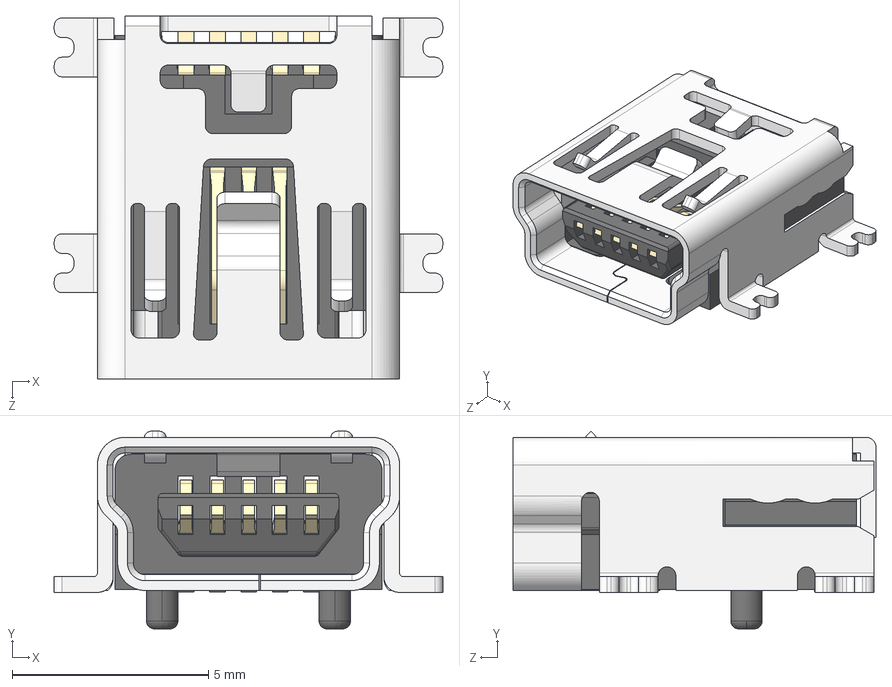
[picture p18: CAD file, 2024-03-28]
Design_Files/PCB_Design_Files/Twitch Switch KiCad/3d-models/690T205-16B-211 - EDAC USB Connector.STEP
9.90 x 5.04 x 9.25 mm
Insulator 690T205-X6B-211
Contact 690T205-X6B-211 x 5
Shell 690T205-X6B-211

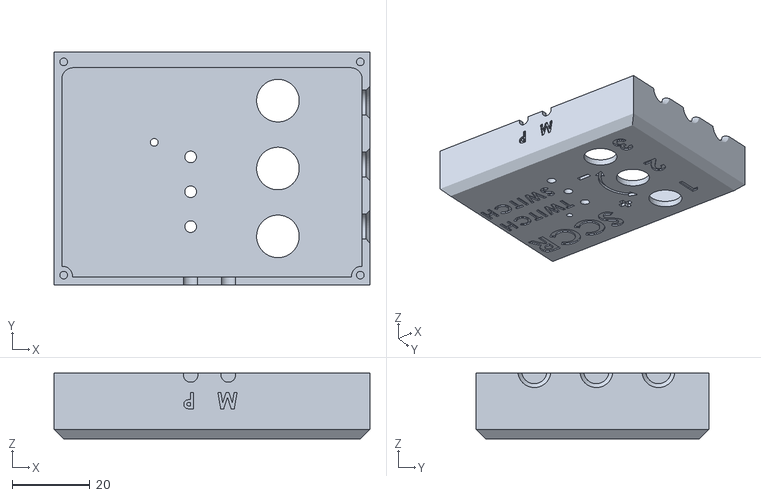
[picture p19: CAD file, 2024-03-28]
Build_Files/3D_Printing_Files/Twitch_Switch_Controller_Top_v3.STL
81.5 x 60.0 x 17.0

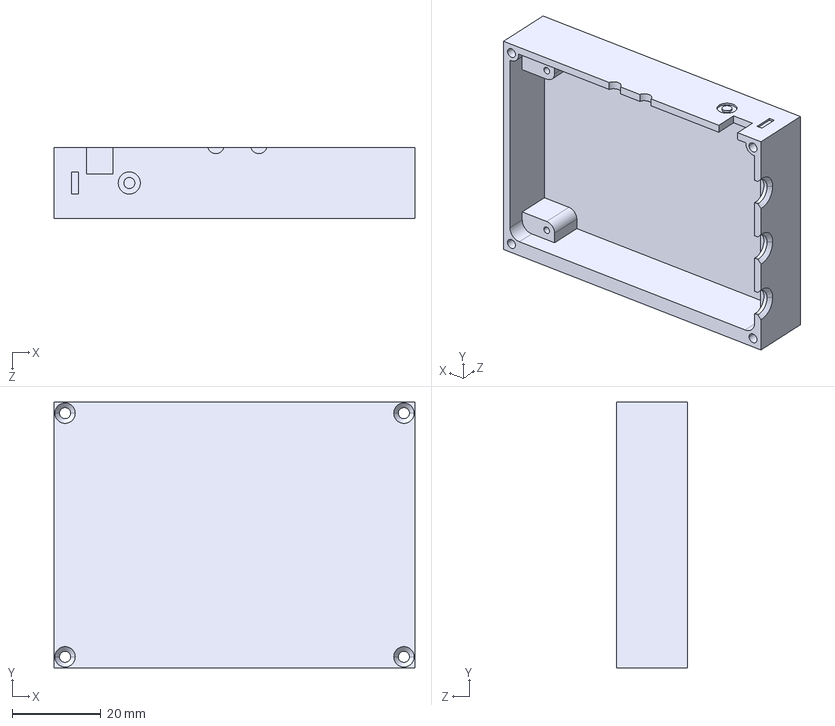
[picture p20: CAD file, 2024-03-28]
Design_Files/CAD_Design_Files/Step/Twitch_Switch_Controller_Base_V3.STEP
81.5 x 60.0 x 16.0 mm

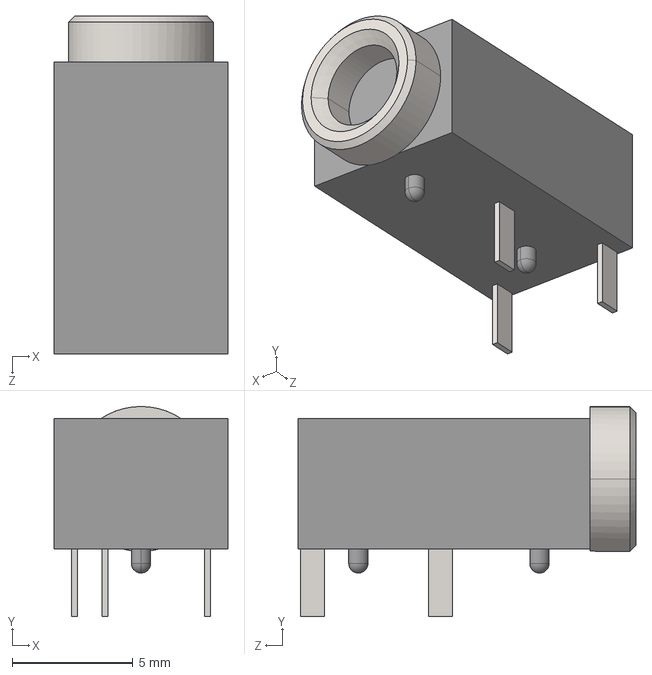
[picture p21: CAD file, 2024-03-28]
Design_Files/PCB_Design_Files/Twitch Switch Base KiCad/3d models/STX-3000.STEP
7.20 x 8.70 x 14.0 mm

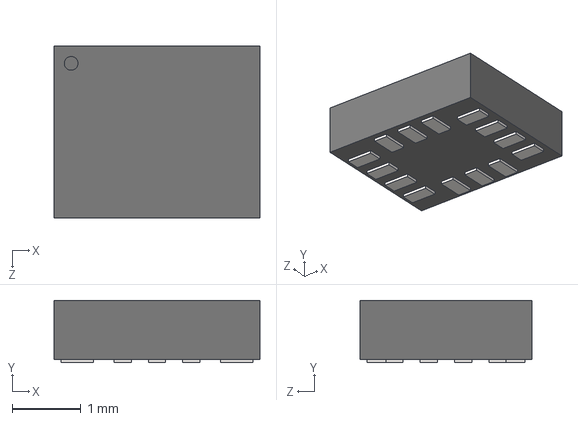
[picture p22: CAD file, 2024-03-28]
Design_Files/PCB_Design_Files/Twitch Switch KiCad/3d-models/LSM6DSM.STEP
3.00 x 0.91 x 2.50 mm

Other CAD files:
Build_Files/3D_Printing_Files/Twitch_Switch_Sensor_Bottom_v3.stl
Design_Files/CAD_Design_Files/Step/Twitch_Switch_Controller_Top_V3.STEP
Build_Files/3D_Printing_Files/Twitch_Switch_Controller_Knob_v3.stl
Build_Files/3D_Printing_Files/Twitch_Switch_Controller_Bottom_v3.STL
Build_Files/3D_Printing_Files/Twitch_Switch_Sensor1_Top_v3.stl
Build_Files/3D_Printing_Files/Twitch_Switch_Sensor2_Top_v3.stl
Design_Files/CAD_Design_Files/SolidWorks/Twitch_Switch_Controller_Base_V3.SLDPRT
Design_Files/CAD_Design_Files/SolidWorks/Twitch_Switch_Controller_Top_V3.SLDPRT
Design_Files/CAD_Design_Files/SolidWorks/Twitch_Switch_Sensor1_Lid.SLDPRT
Design_Files/CAD_Design_Files/SolidWorks/Twitch_Switch_Sensor2_Lid.SLDPRT
Design_Files/CAD_Design_Files/SolidWorks/Twitch_Switch_Sensor3_Lid.SLDPRT
Design_Files/CAD_Design_Files/Step/Twitch_Switch_Sensor3_Lid.STEP
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

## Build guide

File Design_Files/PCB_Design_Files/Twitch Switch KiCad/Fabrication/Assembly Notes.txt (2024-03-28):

Parts J2, J3, XA1, and SW1 are populated by the user and will not be assembled by JLCPCB.
Part J3 is not depicted in "Component Placement.pdf" because it is on the bottom of the PCB.
Paste should not be placed on A0, A1, and A2 jumpers below U1. This is for user configuration and will be soldered by the user for multi-channel use.

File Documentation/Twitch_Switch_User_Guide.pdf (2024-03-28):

V3.0 | MARCH 2024

## Twitch Switch

## USER GUIDE

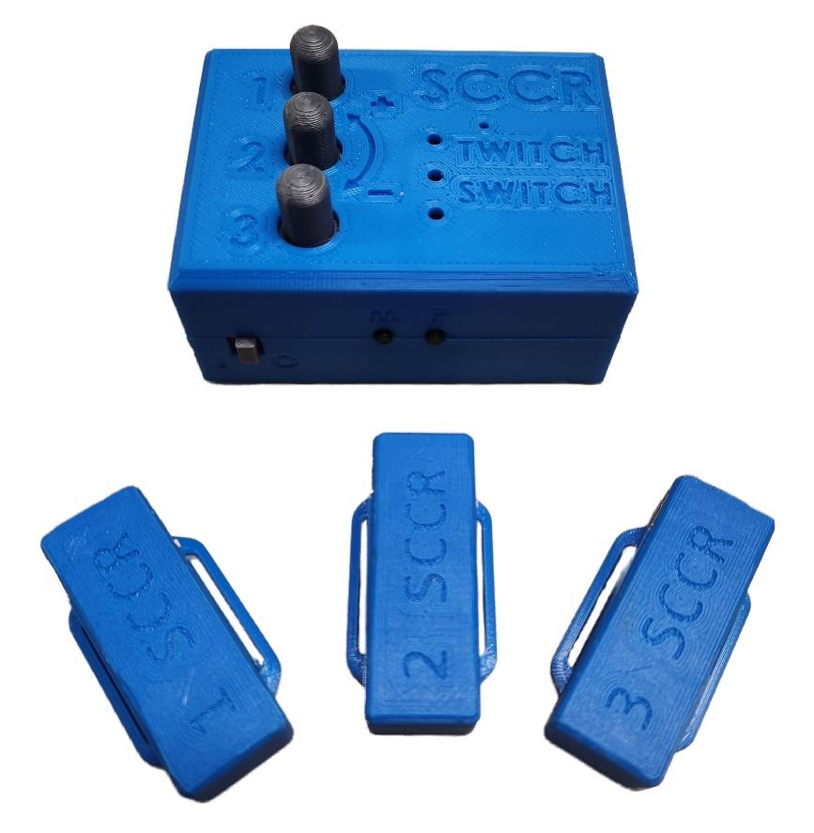
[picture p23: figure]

© 2024 by Stan Cassidy Centre for Rehabilitation This work is licensed under the CC BY SA 4.0 License: http://creativecommons.org/licenses/by-sa/4.0
Files available at https://github.com/makersmakingchange/Twitch-Switch | Page 1 of 16

# Twitch Switch User Guide

V3.0 – March 2024

## USER GUIDE

Files available at https://github.com/makersmakingchange/Twitch-Switch | Page 2 of 16

## Contents

Disclaimer/Assumption of Risk | 3
Introduction | 4
Features | 4
Controller Features | 5
Sensor Features | 6
Usage | 7
Compatibility | 7
Sensor Placement | 7
Setup Guide | 8
Charging Instructions | 9
Manual Calibration | 10
Controlling Switch Adapted Devices | 10
Connecting to Computer, Tablet, or Smart Phone | 12
Connecting to Host Device Using Bluetooth | 12
Connecting to Host Device Through USB | 12
Operating Modes | 13
Overview | 13
Mouse Mode | 13
Tablet Mode | 13
Keyboard Mode | 14
Profiles | 14
Troubleshooting | 15
Troubleshooting Guide | 15
Performing a Factory Reset | 15
Cleaning and Maintenance | 15
Specifications | 16

## USER GUIDE

Files available at https://github.com/makersmakingchange/Twitch-Switch | Page 3 of 16

## Disclaimer/Assumption of Risk

### The Twitch Switch device is not to be used in life support or life safety applications. Such use is entirely at the User’s risk, and the User agrees to defend, indemnify and hold harmless the Stan Cassidy Center for Rehabilitation from any and all damages, claims, suits, or expenses resulting

from such use.

## USER GUIDE

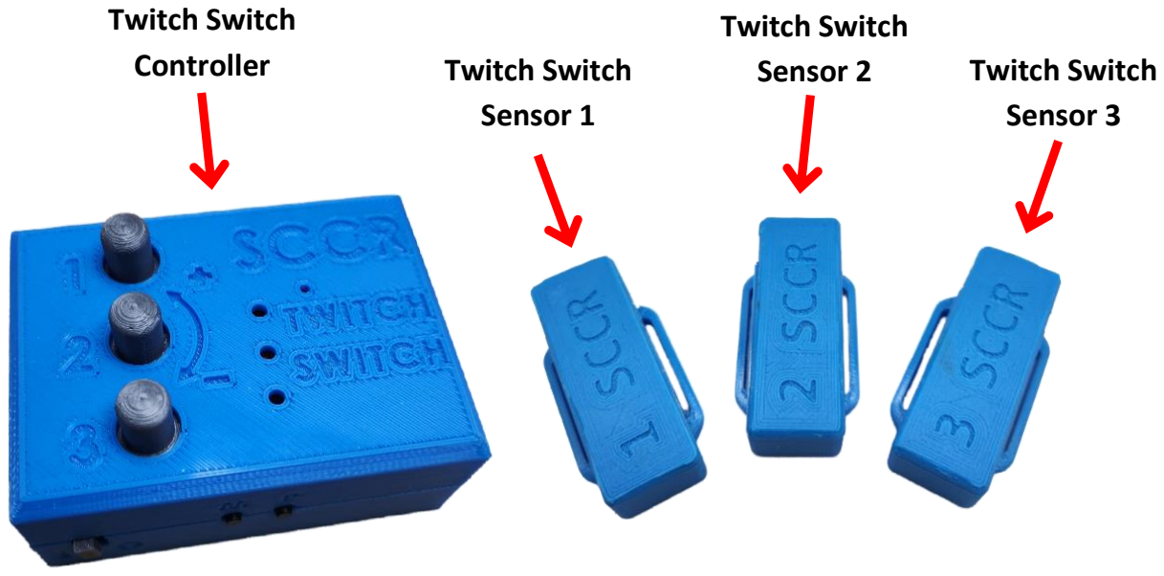
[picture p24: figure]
Twitch Switch; Controller; Sensor 1; Sensor 2; Sensor 3

Files available at https://github.com/makersmakingchange/Twitch-Switch | Page 4 of 16

## Introduction

The Twitch Switch device is designed to address the needs of people with very limited movement capabilities. It operates by using wireless sensors placed on the body to detect small movements and relaying them to a controller that operates your switch-adapted devices or a personal computer. You can use just one, two, or all three sensors at the same time to match your needs.

The following is an easy setup guide to get you started. You will need a micro-USB cable, a mini-USB cable, and up to three audio cables, depending on how you wish to use your device.

You will also need to provide materials to secure your sensors in place; see suggested materials on page 7.

## Features

## USER GUIDE

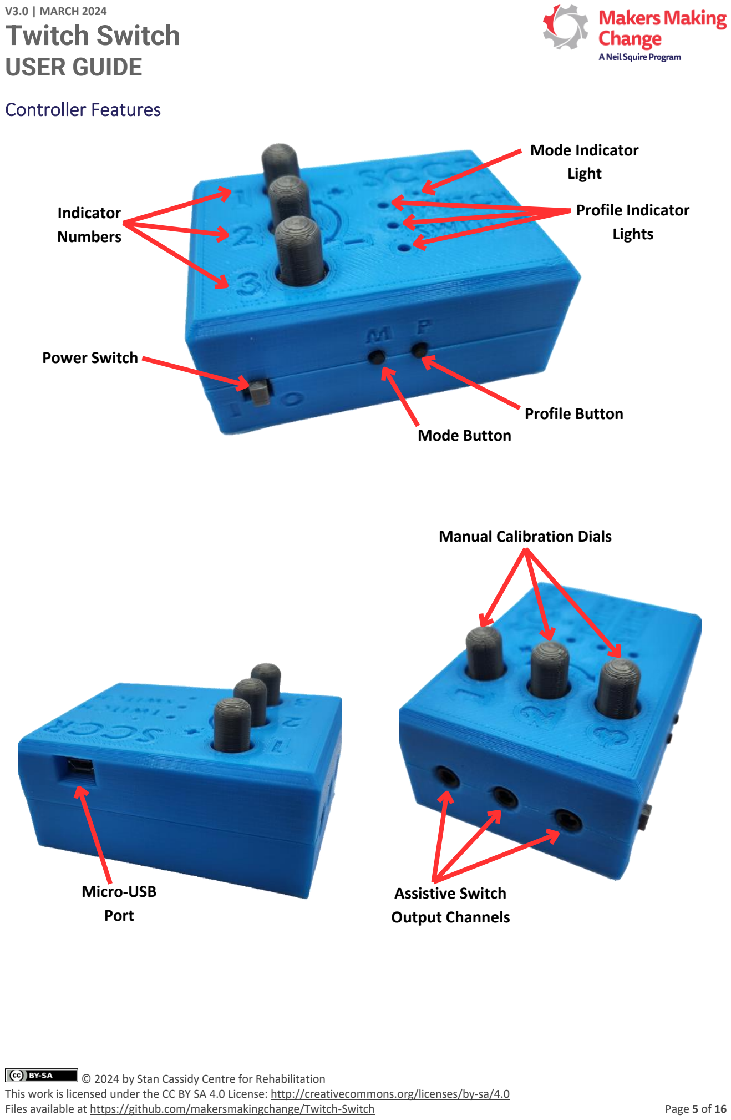
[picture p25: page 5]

Files available at https://github.com/makersmakingchange/Twitch-Switch | Page 5 of 16

### Controller Features

Indicator
Numbers

Power Switch

Mode Indicator
Light

Profile Indicator
Lights

Profile Button
Mode Button

Micro-USB
Port

Manual Calibration Dials

Assistive Switch
Output Channels

## USER GUIDE

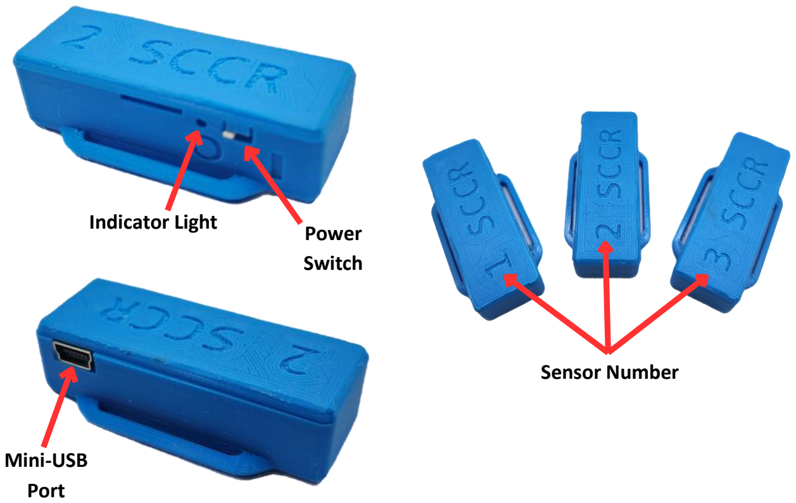
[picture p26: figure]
Indicator Light; Power; Switch; Mini-USB Port; Sensor Number

Files available at https://github.com/makersmakingchange/Twitch-Switch | Page 6 of 16

### Sensor Features

## USER GUIDE

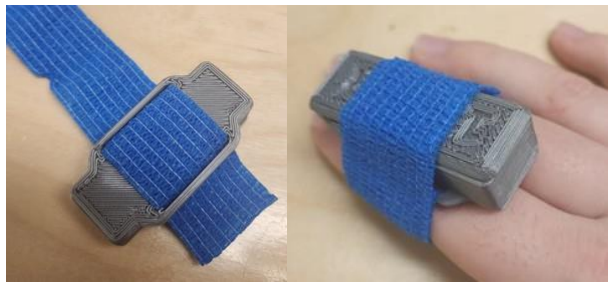
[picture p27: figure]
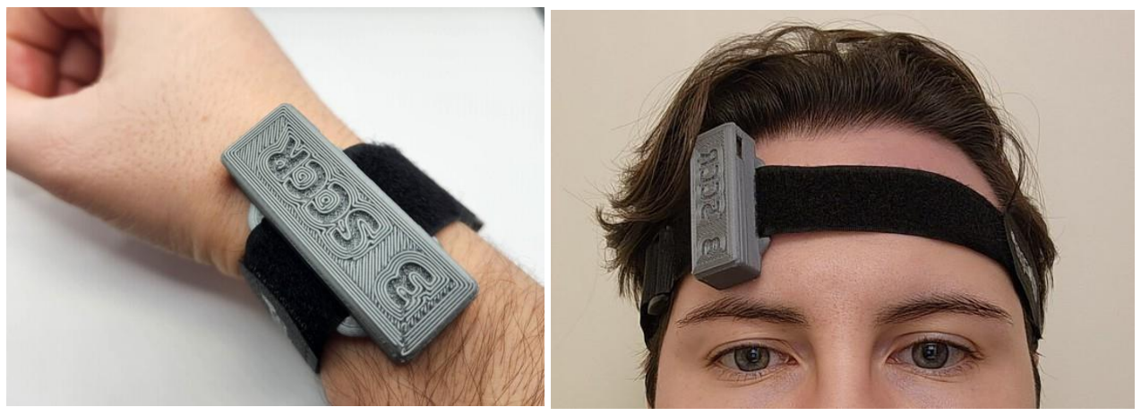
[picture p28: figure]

Files available at https://github.com/makersmakingchange/Twitch-Switch | Page 7 of 16

## Usage

### Compatibility

The Twitch Switch is compatible with Windows and Mac computers, and both Apple and Android mobile devices.

### Sensor Placement

The sensors can be placed on any site where movement can be controlled and repeated. Typical sites are fingers, wrists, feet, and forehead. Suggested materials for securing the sensors include self-adhesive wrap (commonly referred to as ‘Coban®’), headbands, or other soft straps, but you may use any materials you have at your disposal to secure the sensors in place.

The sensors have built-in band loops the keep them secure, as shown below.

Typical placement on finger using self-adhesive wrap:

Typical placement on the wrist or on the forehead:

## USER GUIDE

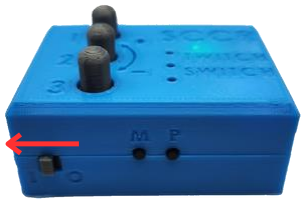
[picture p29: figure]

Files available at https://github.com/makersmakingchange/Twitch-Switch | Page 8 of 16

### Setup Guide

Step 1: Place the sensors on the body anywhere movement can be controlled and repeated. See page 7 for sensor placement suggestions.
Step 2: Power up the sensors by sliding the power switch to the ON position. When a sensor powers up, the indicator light will blink red 5 times and then remain steady.
Step 3: Power-up the controller unit by sliding the power switch to the ON position. The mode light will blink purple intermittently, then will change colour to indicate the mode the device is in (see page 13 for modes). Proceed to the manual calibration step if necessary.

If the light does not blink at all, this indicates a low battery. The device will need to be charged before use; please see the charging instructions on page 9.

## USER GUIDE

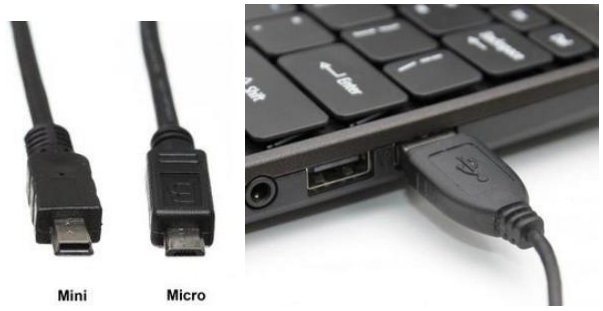
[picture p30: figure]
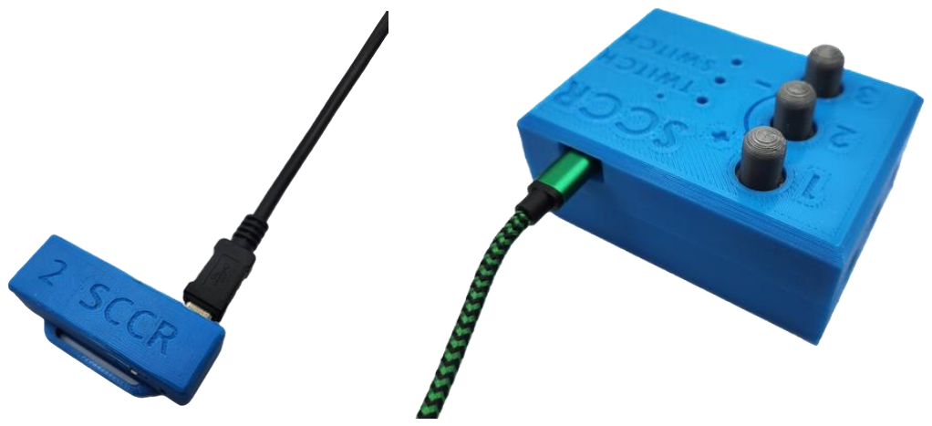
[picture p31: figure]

Files available at https://github.com/makersmakingchange/Twitch-Switch | Page 9 of 16

### Charging Instructions

To charge your devices, first locate the appropriate charging cables. You will need a mini-USB cable to charge the sensors and a micro-USB cable to charge the controller.

Step 1: Plug the USB cable into a USB wall adapter or other USB outlet such as on your desktop or laptop.
Step 2: Connect the appropriate USB cable to the corresponding device. Charging can take up to one hour.

## USER GUIDE

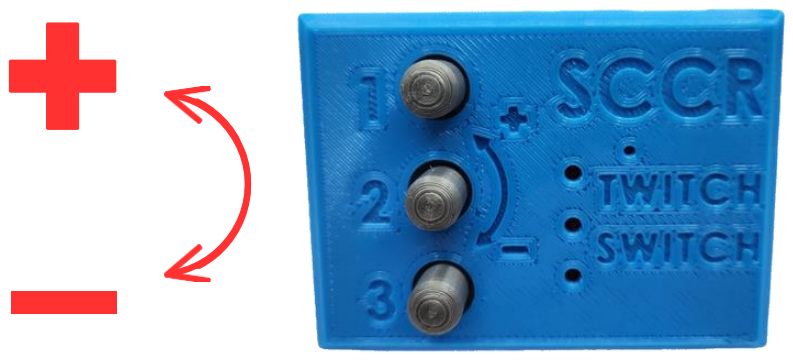
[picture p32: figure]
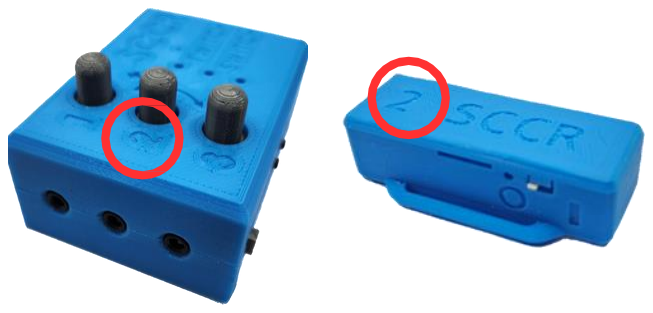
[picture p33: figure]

Files available at https://github.com/makersmakingchange/Twitch-Switch | Page 10 of 16

### Manual Calibration

To customize the sensors to the user’s movements, a manual calibration should be performed. This will allow the sensors to detect the user’s movements more accurately without “misfiring”.

To increase the sensitivity of a sensor to small or slow movements, turn the corresponding dial counterclockwise. To reduce the sensitivity of a sensor, turn the corresponding dial clockwise. Calibration settings are automatically saved to the current profile.

### Controlling Switch Adapted Devices

The Twitch Switch can be used to control switch-adapted devices such as toys, a doorbell, lamp, fan, etc. The Twitch Switch can control up to three adapted devices at one time. It functions by replacing the traditional wired assistive switch, such as a Buddy Button™. Note that your device must already be switch- adapted to be used with the Twitch Switch.

To connect to your adapted device, you will need up to three male to male audio cables. Connect one end to the desired channel on the Twitch Switch and the other in the adapted device. Note: the number above the channel indicates the sensor that controls it.

## USER GUIDE

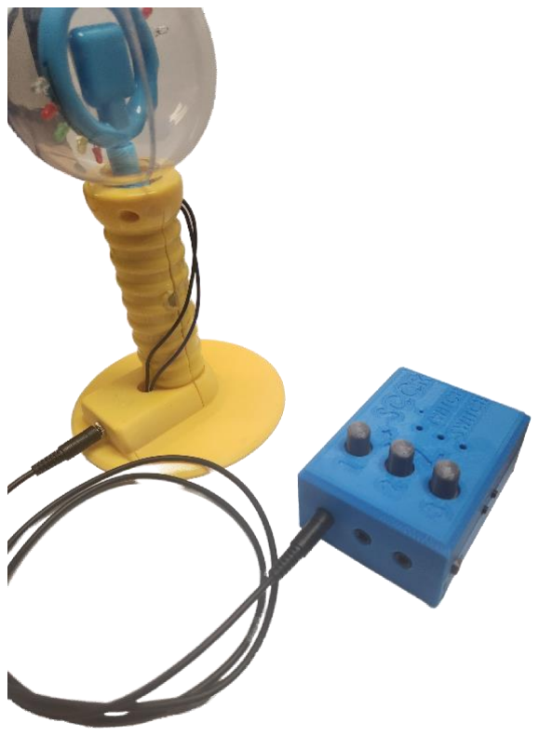
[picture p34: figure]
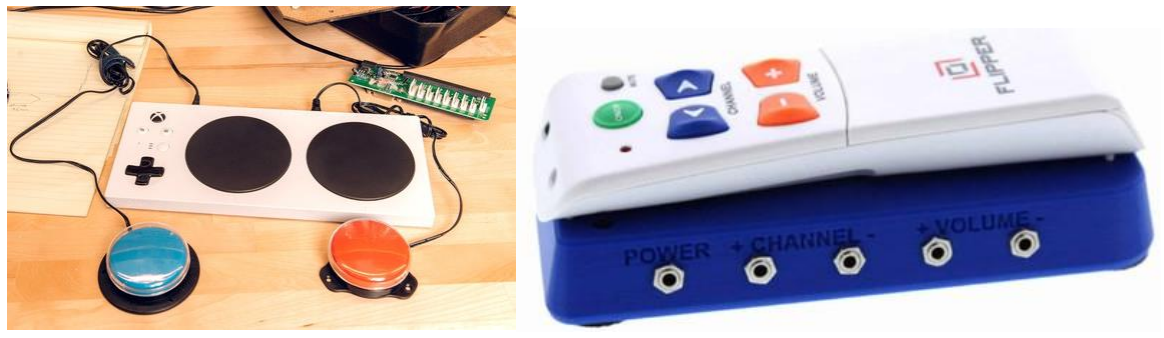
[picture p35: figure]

Files available at https://github.com/makersmakingchange/Twitch-Switch | Page 11 of 16

Here is a photo of the Twitch Switch being used to controller a switch adapted toy:

Below are some examples of other adapted devices that can be used with the Twitch Switch. The Xbox Adaptive Controller® can be used with several gaming systems, such as the Xbox One and Windows 10/11 PCs. The adapted media remote may be used to change channels or adjust the volume on a TV. The Twitch Switch can control up to three of functions on either of these controllers.

## USER GUIDE

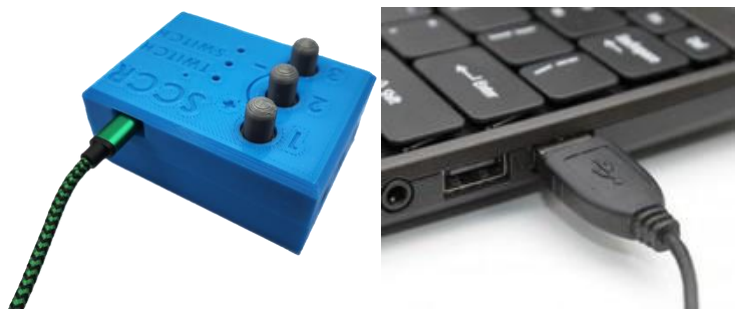
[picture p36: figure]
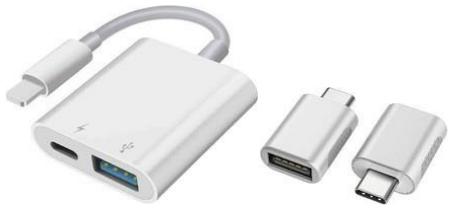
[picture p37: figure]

Files available at https://github.com/makersmakingchange/Twitch-Switch | Page 12 of 16

### Connecting to Computer, Tablet, or Smart Phone

There are two ways you can connect the Twitch Switch to a digital device such as a computer, tablet, or smart phone; either via Bluetooth or through a wired connection.

Connecting to Digital Device Using Bluetooth
To pair the Twitch Switch with your computer, tablet, or smart phone via Bluetooth, simply locate the Bluetooth Settings of your device. The Twitch Switch is always in “pairing” mode and should automatically appear in this menu as an available device. Select the Twitch Switch and pairing will occur.

If the Twitch Switch is unable to pair, ensure you don’t already have it connected to another device. If so, go into the devices settings and remove or disconnect the Twitch Switch, before attempting to connect to a new device.

Connecting to Digital Device Through USB
You may also connect the Twitch Switch to your computer, tablet, or smart phone using a micro-USB cable along with an adapter specific to your device, if necessary.

If using an Apple™ product, you will need to connect your micro-USB cord to the appropriate USB adapter for the Lift Switch to function properly as a mouse click device. Some potential adapters are pictured below:

If you are using an Apple™ device, refer to the online instructions found here: https://support.apple.com/en-us/HT211008 for mouse functions, and https://support.apple.com/en-ca/HT201370 for Switch Control functions.

## USER GUIDE

Files available at https://github.com/makersmakingchange/Twitch-Switch | Page 13 of 16

### Operating Modes

Overview
When connecting to a computer, tablet, or smart phone, there are three different modes that can be used, described in the table below. To change the operating mode, press the Mode button (marked with an “M”) on the Twitch Switch Controller, the Mode Indicator Light will then change colours to represent the current mode.
Operating Mode | Mode Indicator Light Colour | Mode Overview
Mouse Mode | Green | Performs mouse movement and mouse left click.
Tablet Mode | Blue | Performs mouse left click, scroll down, and scroll up.
Keyboard Mode | Yellow | Performs presses of ‘F1’, ‘F2’, and ‘F3’ keys.

Mouse Mode
When the Twitch Switch is in Mouse Mode, the mode indicator light will be green. This mode allows users to control a mouse cursor using the sensors. Twitching the sensors will cause the following actions:
Sensor Number | Action
1 Performs mouse left click
2 Moves cursor left and right
3 Moves cursor up and down

Sensor 1 creates a mouse ‘click’. There is a short delay between clicks to prevent accidental double-clicking. If you are using applications that require double-clicking, it is recommended that you change the settings of your computer or tablet to only require a single-click to open an item.

Sensors 2 and 3 move the cursor around the screen. Sensor 2 moves the cursor left and right, while sensor 3 moves the cursor up and down. Activate sensor 2 or 3 once to start the pointer in their associated direction.

While the cursor is moving, activate any of the three sensors to stop the cursor. Activate sensor 2 or 3 again to start the cursor moving in the opposite direction. Repeat these steps as necessary.

Tablet Mode
When the Twitch Switch is in Tablet Mode, the mode indicator light will be blue. This mode allows users to navigate apps on a tablet or iPad. Twitching the sensors will cause the following actions:
Sensor Number | Action
1 Performs mouse left click
2 Scrolls down on the screen (on a tablet this will act like scrolling up) 3 Scrolls up on the screen (on a tablet this will act like scrolling down)

## USER GUIDE

Files available at https://github.com/makersmakingchange/Twitch-Switch | Page 14 of 16

Sensor 1 creates a ‘click’. There is a short delay between clicks to prevent accidental double-clicking. If you are using applications that require double-clicking, it is recommended that you change the settings of your tablet to only require a single-click to open an item.

Sensor 2 scrolls down the screen, while sensor 3 scrolls up the screen. Note that the scroll directions may be reversed when using a tablet instead of a computer.

Keyboard Mode
When the Twitch Switch is in ‘Keyboard Mode’, the mode indicator light will be yellow. This mode allows users to create a more custom experience by mapping actions to keys, and is often used for switch control. The sensor outputs are the following:
Sensor Number | Action
1 Performs keyboard press of ‘F1’ key
2 Performs keyboard press of ‘F2’ key
3 Performs keyboard press of ‘F3’ key
A great application of keyboard mode is Switch Control. Switch Control is an accessibility function found on Apple™ devices that allows the user to navigate their iPad or iPhone with switches such as the Twitch Switch. For more information on Switch Control, see the following information from Apple™:

https://support.apple.com/en-us/HT201370

### Profiles

The controller can store your settings for up to three separate profiles. Both your sensors’ calibration settings and mode are saved to the profile. This can reduce how often the user must calibrate their sensors. The following are some examples on how to use multiple profiles.

Assign profiles to different positions: Profile 1 calibrated for a seated position, Profile 2 calibrated for laying down.

Assign profiles to different levels of fatigue: Profile 1 calibrated for low fatigue, Profile 2 calibrated for higher fatigue, Profile 3 calibrated to highest fatigue. This would allow the user to switch profiles depending on their level of fatigue at a given time.

Assign profiles to different functions: Profile 1 calibrated for use as a cursor on a computer or tablet, Profiles 2 and 3 calibrated for use with other accessible devices.

Change the current profile by pressing the Profile button. The profile indicator light will change to indicate the selected profile.

## USER GUIDE

Files available at https://github.com/makersmakingchange/Twitch-Switch | Page 15 of 16

## Troubleshooting

### Troubleshooting Guide

Problem | Possible Cause | Solution
Twitch Switch not responding to any movement | Sensor(s) or controller are not turned on or not charged | Ensure sensors and controller are turned on and fully charged
| Sensor(s) and controller are too far apart | Bring sensor(s) and controller closer together
Twitch Switch "firing" randomly | Sensitivity of sensor(s) is too high | Perform manual calibration to decrease sensitivity or reset the device
Twitch Switch not responding to every movement, only some | Sensitivity of sensor(s) is too low | Perform manual calibration to increase sensitivity or reset the device
| Sensor(s) and controller are too far apart | Bring sensor(s) and controller closer together

### Performing a Factory Reset

If the device becomes unresponsive or you are having difficulty calibrating the sensors, you may perform a factory reset to restore the base settings of the device. Note that all stored settings for all three profiles will be lost.

Step 1: Turn the device off.
Step 2: Hold down the Mode and Profile buttons.
Step 3: While holding down the buttons, turn the device on.
Step 4: The Mode light will blink purple intermittently, then will blink red three times, indicating a factory reset.

## Cleaning and Maintenance

To clean your Twitch Switch controller and sensors, wipe them with a damp cloth or disinfecting wipe.

The Twitch Switch and the sensors are NOT WATERPROOF – DO NOT IMMERSE THEM IN WATER. This would cause permanent damage to the devices.

Ensure device and sensors are powered OFF after each use to maintain battery life. Charge devices between uses of over one hour.

## USER GUIDE

Files available at https://github.com/makersmakingchange/Twitch-Switch | Page 16 of 16

## Specifications

Controller:
Dimension | Value
Mass | 125 g
Height (without knobs) | 3.3 cm
Height (with knobs) | 4.5 cm
Length | 8.1 cm
Width | 6.0 cm

Sensors:
Dimension | Value
Mass | 15 g
Height | 1.5 cm
Length | 5.1 cm
Width (without strap loops) | 1.9 cm
Width (with strap loops) | 2.6 cm

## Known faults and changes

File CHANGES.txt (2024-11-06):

Version 3.1 | 2024-11-06
 *Sensor programmer:
	- Updated the wiring diagram and instructions that were not working before
	- Removed resistor
	- Replaced the diode with one that is more maker friendly

 - Maker Guide
	- Corrected the wiring diagram for the Sensor Programmer
	- Corrected the board name to select when programming the controller
 - BOM
	- Removed resistor from sensor programmer
	- Changed the diode to one that is more maker friendly

Version 3.0 | 2024-03-28
 - Initial Release

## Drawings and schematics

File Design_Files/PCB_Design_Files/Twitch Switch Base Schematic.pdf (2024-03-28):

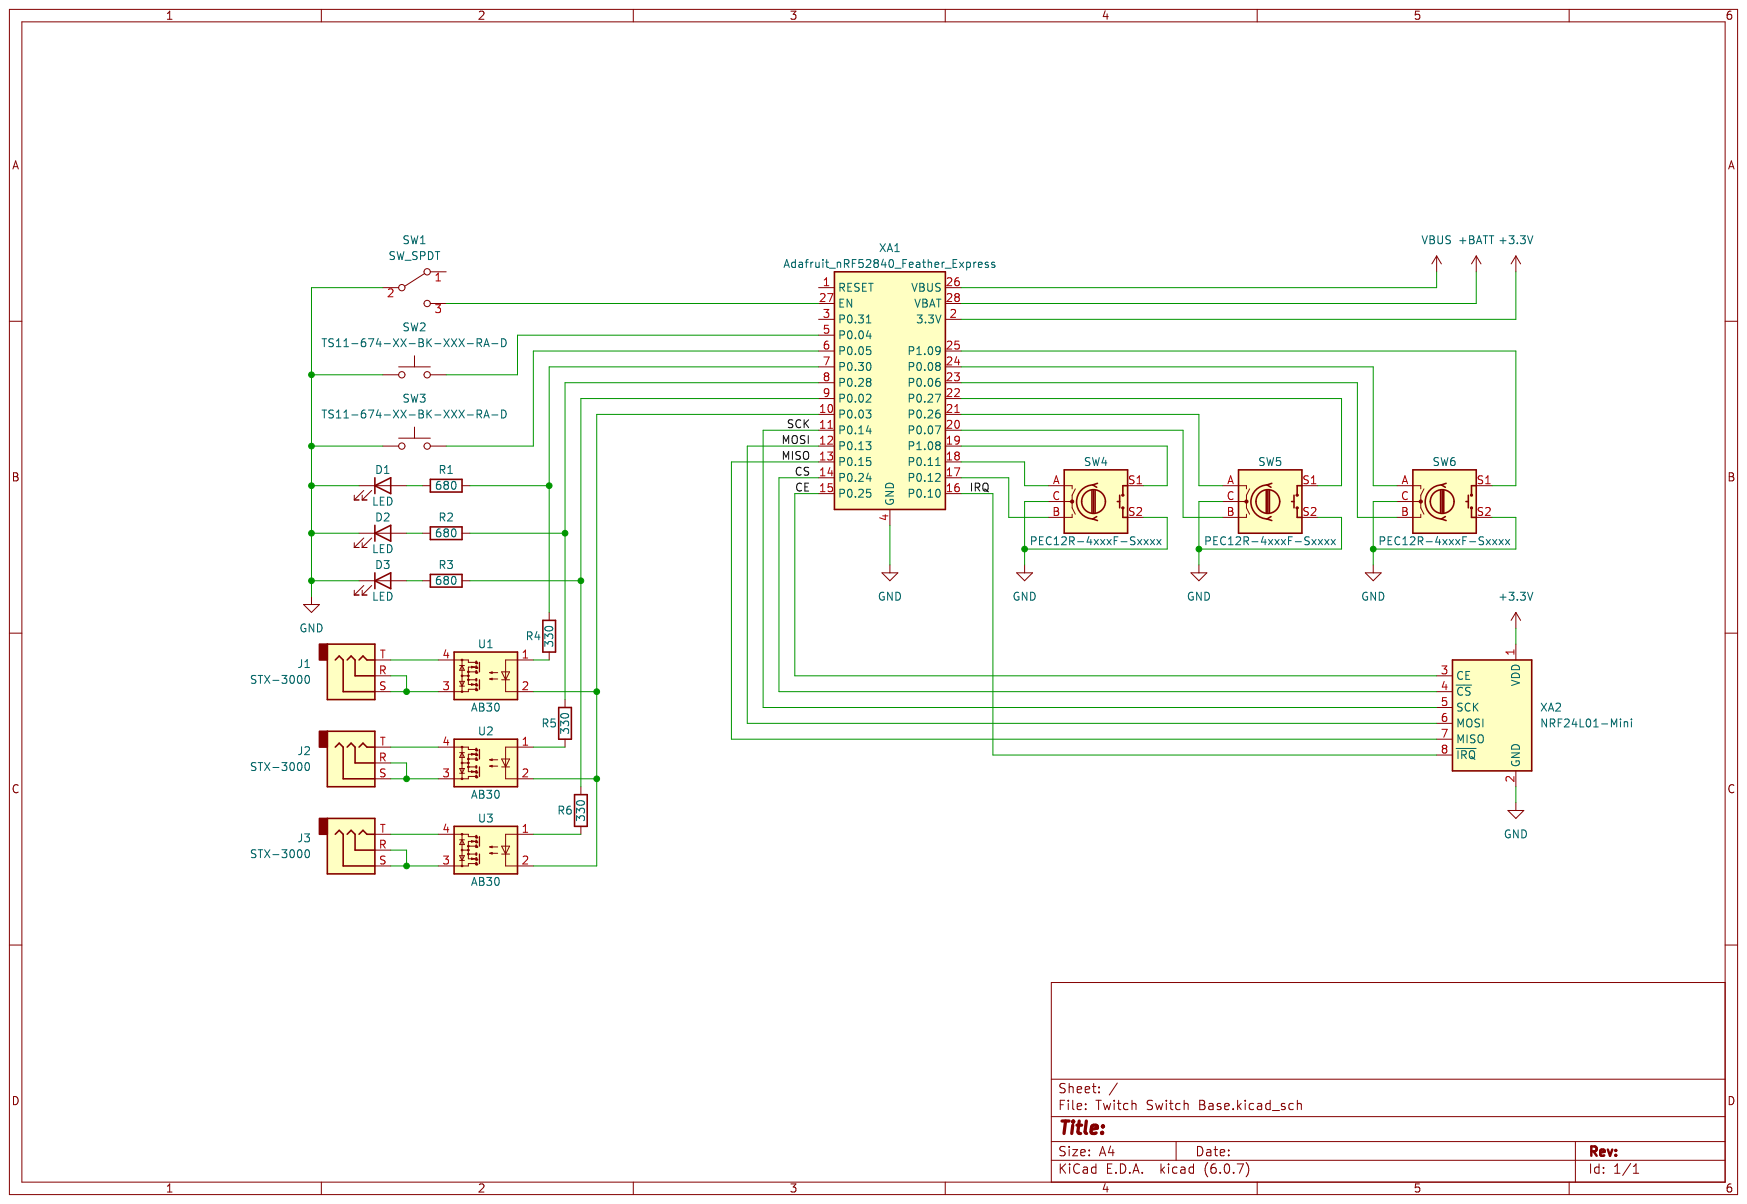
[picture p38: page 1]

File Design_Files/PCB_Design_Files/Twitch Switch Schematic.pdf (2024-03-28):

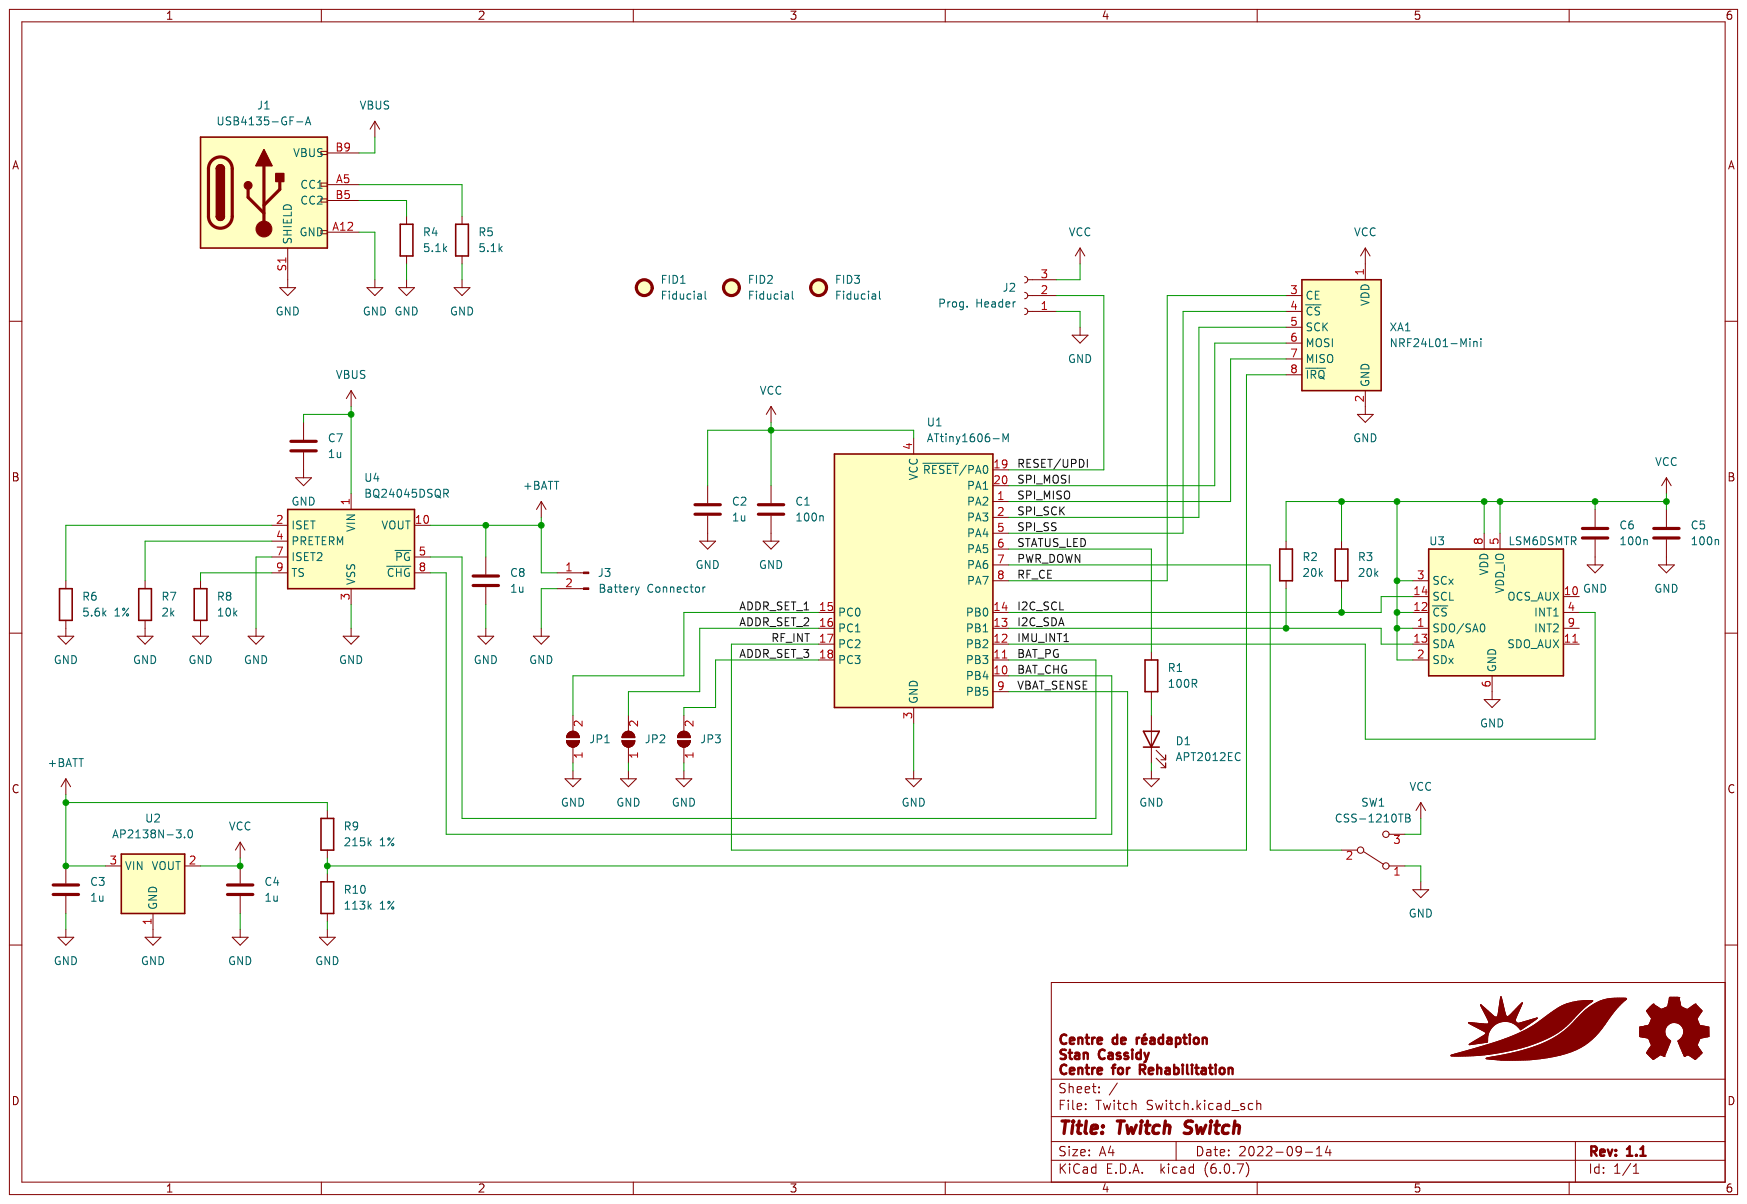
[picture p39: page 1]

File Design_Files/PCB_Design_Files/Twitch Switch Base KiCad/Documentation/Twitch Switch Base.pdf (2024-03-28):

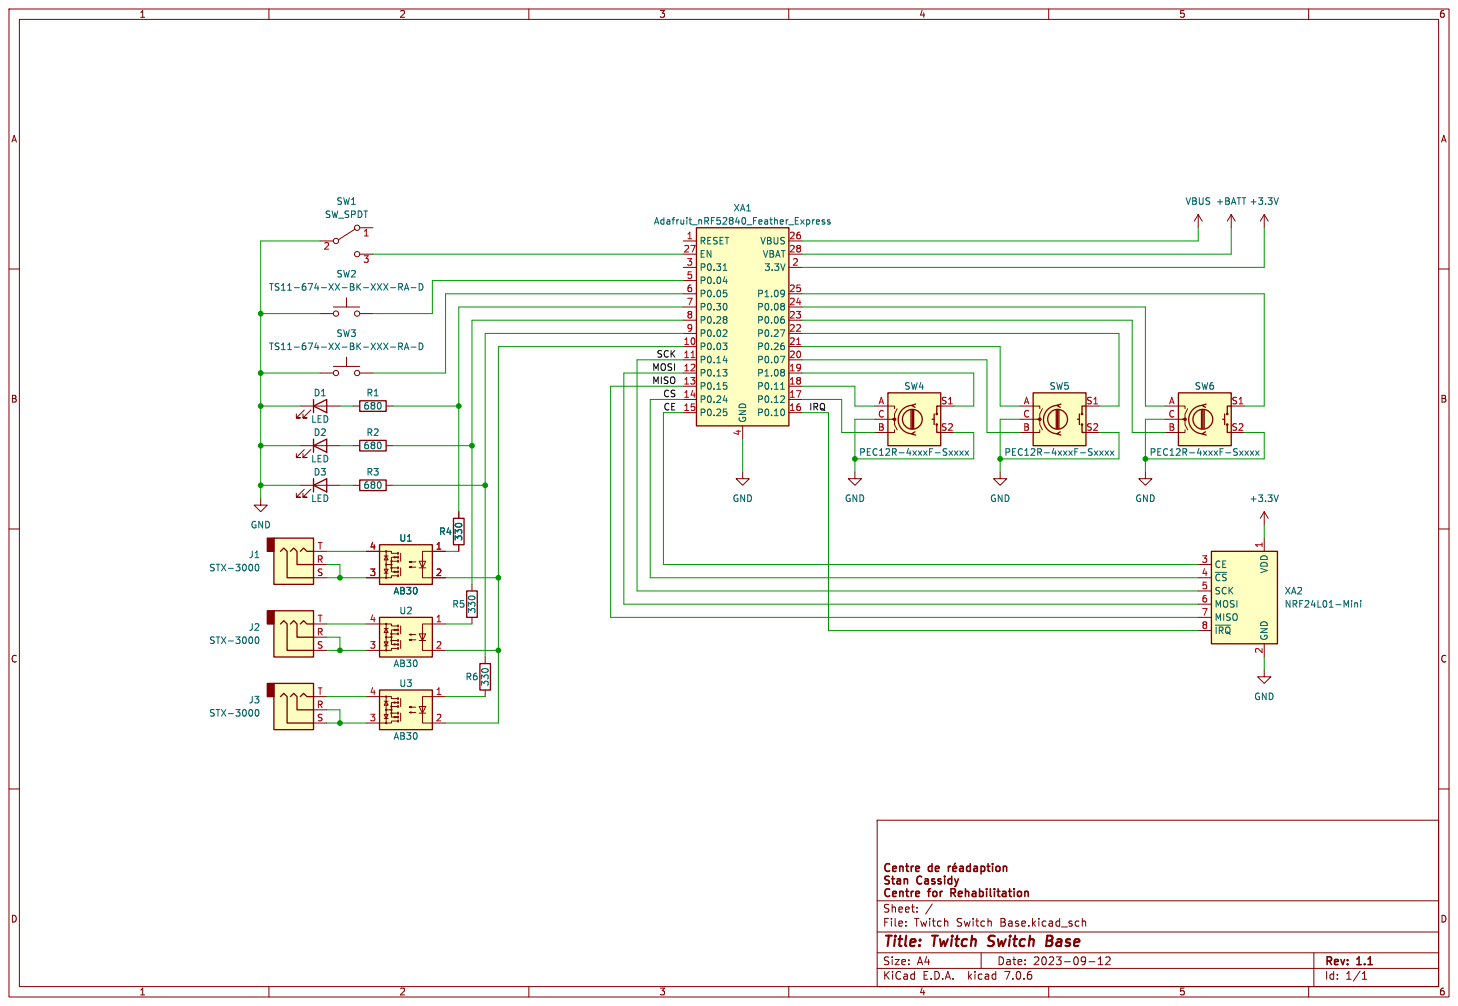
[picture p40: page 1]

2 CE 3 ~{CS} 4 SCK 5 MOSI 6 MISO 7 ~{IRQ} 8 XA2 NRF24L01-Mini 1

Id: 1/1 Title: Twitch Switch Base

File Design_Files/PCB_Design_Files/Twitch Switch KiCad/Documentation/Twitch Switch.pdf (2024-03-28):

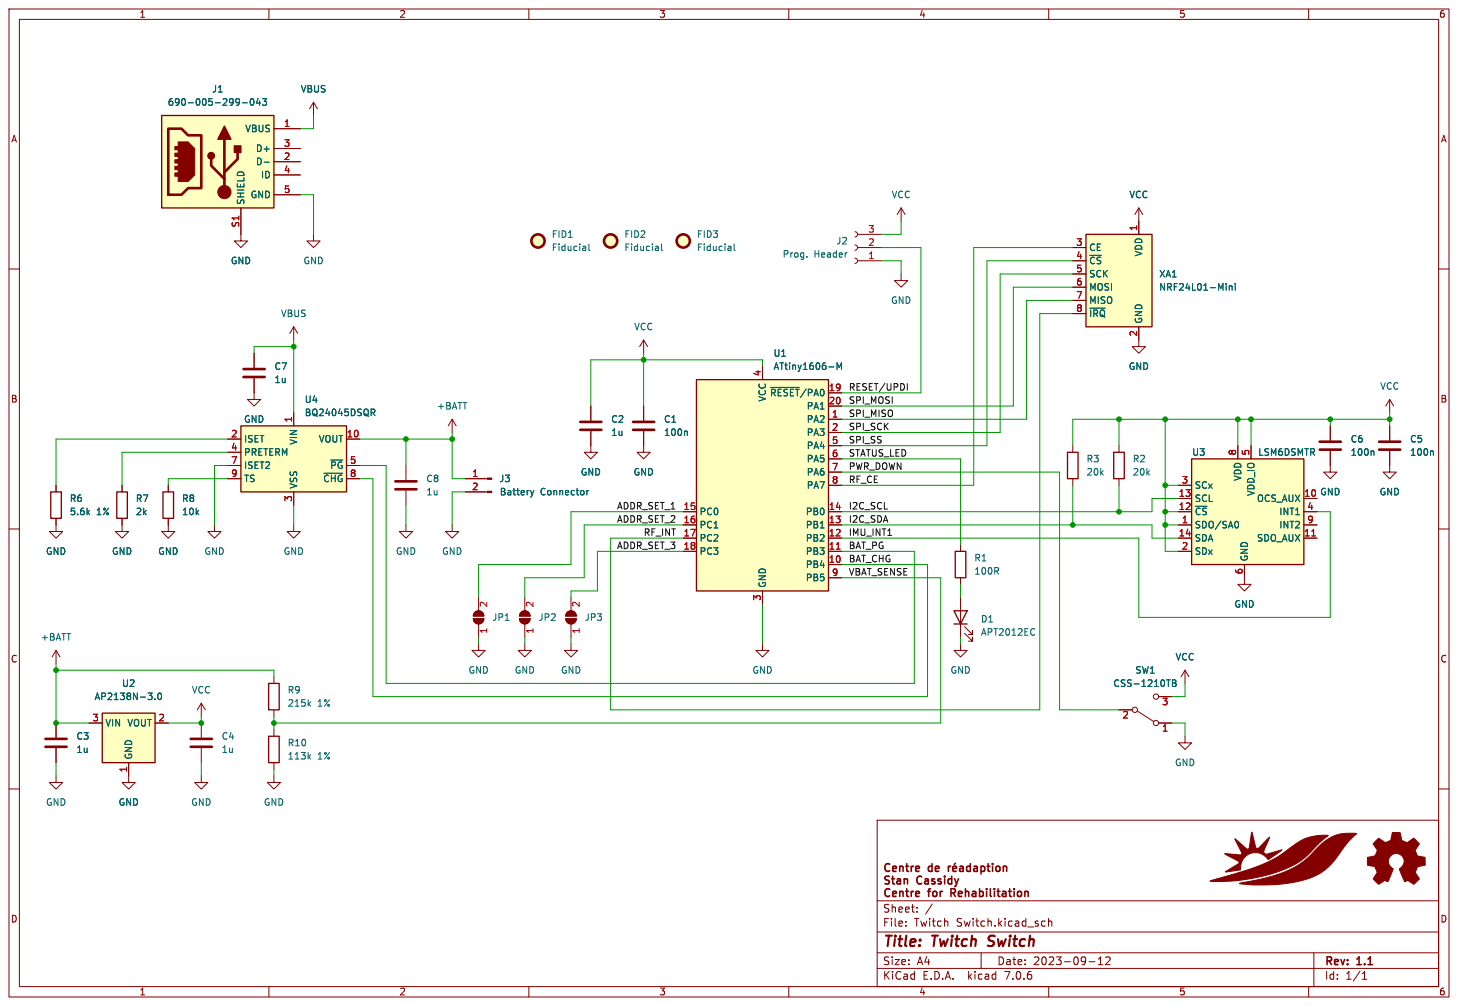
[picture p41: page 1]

FID3 Fiducial FID2 Fiducial VCC GND

2 CE 3 ~{CS} 4 SCK 5 MOSI 6 MISO 7 ~{IRQ} 8 XA1 NRF24L01-Mini GND

2 CE 3 ~{CS} 4 SCK 5 MOSI 6 MISO 7 ~{IRQ} 8 GND

Id: 1/1 Title: Twitch Switch

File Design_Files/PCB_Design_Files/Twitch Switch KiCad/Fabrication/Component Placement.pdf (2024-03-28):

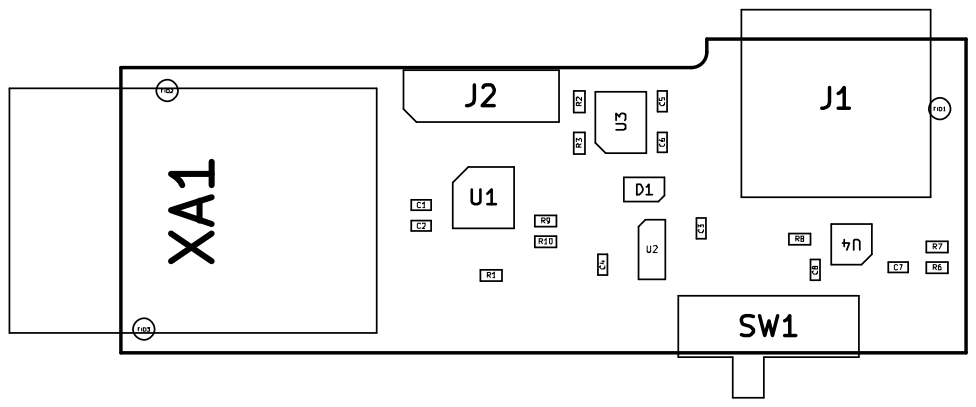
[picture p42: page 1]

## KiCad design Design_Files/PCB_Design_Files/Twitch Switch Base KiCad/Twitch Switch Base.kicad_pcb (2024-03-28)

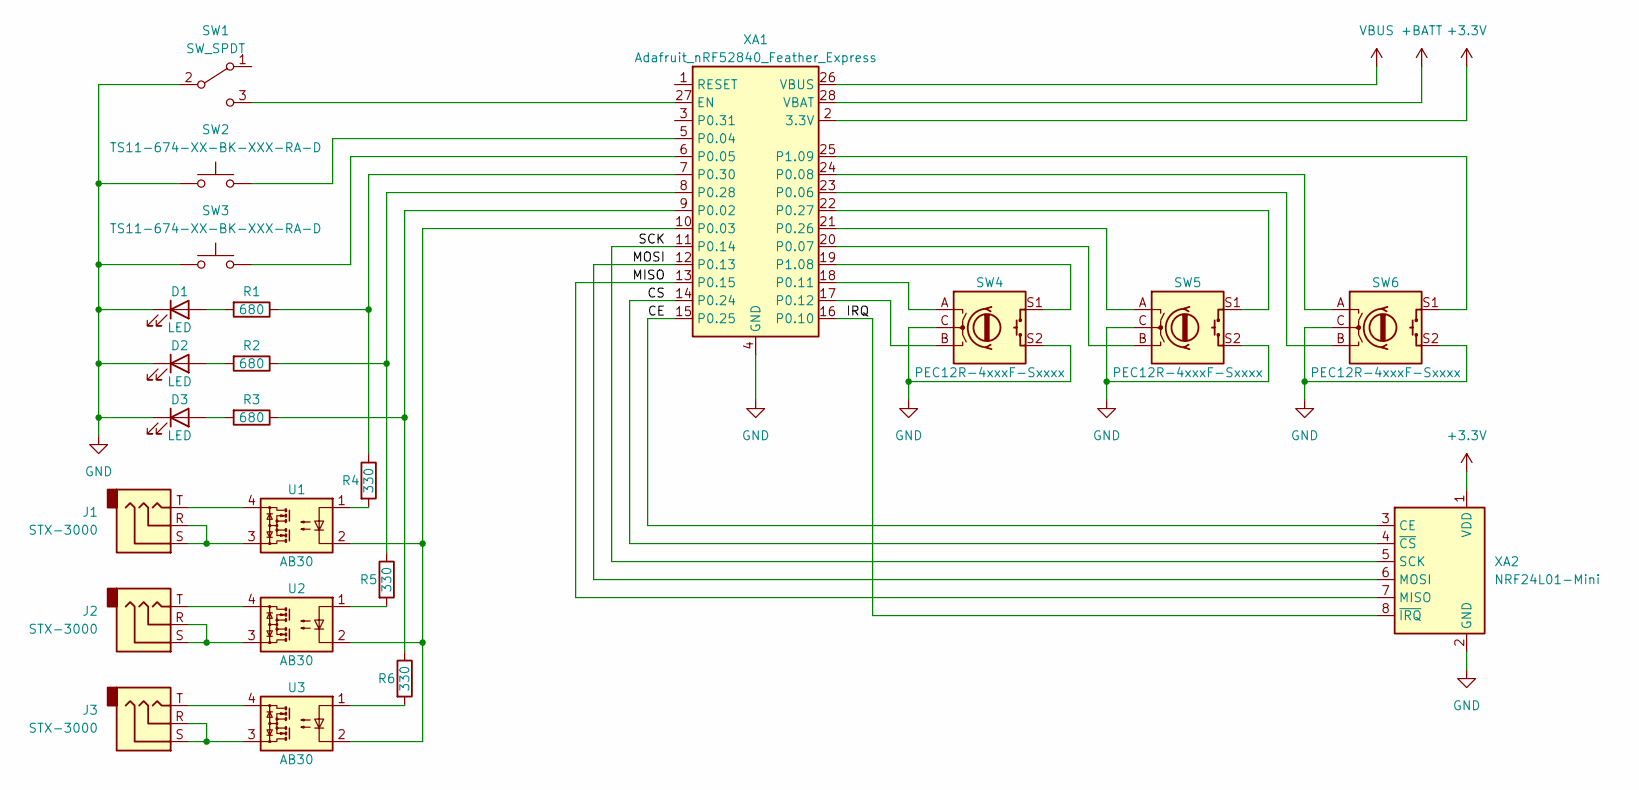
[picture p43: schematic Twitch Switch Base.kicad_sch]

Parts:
D1, D2, D3: LED; LED_D5.0mm
J1, J2, J3: STX-3000
R1, R2, R3: 680; R_Axial_DIN0207_L6.3mm_D2.5mm_P7.62mm_Horizontal
R4, R5, R6: 330; R_Axial_DIN0207_L6.3mm_D2.5mm_P7.62mm_Horizontal
SW1: SW_SPDT; CSS-1210TB
SW2, SW3: TS11-674-XX-BK-XXX-RA-D
SW4, SW5, SW6: PEC12R-4xxxF-Sxxxx
U1, U2, U3: AB30; DIP-4_W7.62mm
XA1: Adafruit_nRF52840_Feather_Express; Adafruit Feather nRF52840 Express
XA2: NRF24L01-Mini

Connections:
+3.3V: XA1.2 (3.3V), XA2.1 (VDD)
+BATT: XA1.28 (VBAT)
/CE: XA1.15 (P0.25), XA2.3 (CE)
/CS: XA1.14 (P0.24), XA2.4 (~CS)
/IRQ: XA1.16 (P0.10), XA2.8 (~IRQ)
/MISO: XA1.13 (P0.15), XA2.7 (MISO)
/MOSI: XA1.12 (P0.13), XA2.6 (MOSI)
/SCK: XA1.11 (P0.14), XA2.5 (SCK)
GND: D1.1 (K), D2.1 (K), D3.1 (K), SW1.2 (B), SW2.1, SW3.1, SW4.C, SW4.MP, SW4.S2, SW5.C, SW5.MP, SW5.S2, SW6.C, SW6.MP, SW6.S2, XA1.4 (GND), XA1.MNT1, XA1.MNT2, XA2.2 (GND), XA2.9 (GND)
unnamed: D1.2 (A), R1.2
unnamed: D2.2 (A), R2.2
unnamed: D3.2 (A), R3.2
unnamed: J1.R, J1.S, U1.3
unnamed: J1.T, U1.4
unnamed: J2.R, J2.S, U2.3
unnamed: J2.T, U2.4
unnamed: J3.R, J3.S, U3.3
unnamed: J3.T, U3.4
unnamed: R1.1, R4.1, XA1.7 (P0.30)
unnamed: R2.1, R5.1, XA1.8 (P0.28)
unnamed: R3.1, R6.1, XA1.9 (P0.02)
unnamed: R4.2, U1.1
unnamed: R5.2, U2.1
unnamed: R6.2, U3.1
unnamed: SW1.3 (C), XA1.27 (EN)
unnamed: SW2.2, XA1.5 (P0.04)
unnamed: SW3.2, XA1.6 (P0.05)
unnamed: SW4.A, XA1.18 (P0.11)
unnamed: SW4.B, XA1.17 (P0.12)
unnamed: SW4.S1, XA1.19 (P1.08)
unnamed: SW5.A, XA1.21 (P0.26)
unnamed: SW5.B, XA1.20 (P0.07)
unnamed: SW5.S1, XA1.22 (P0.27)
unnamed: SW6.A, XA1.24 (P0.08)
unnamed: SW6.B, XA1.23 (P0.06)
unnamed: SW6.S1, XA1.25 (P1.09)
unnamed: U1.2, U2.2, U3.2, XA1.10 (P0.03)
VBUS: XA1.26 (VBUS)

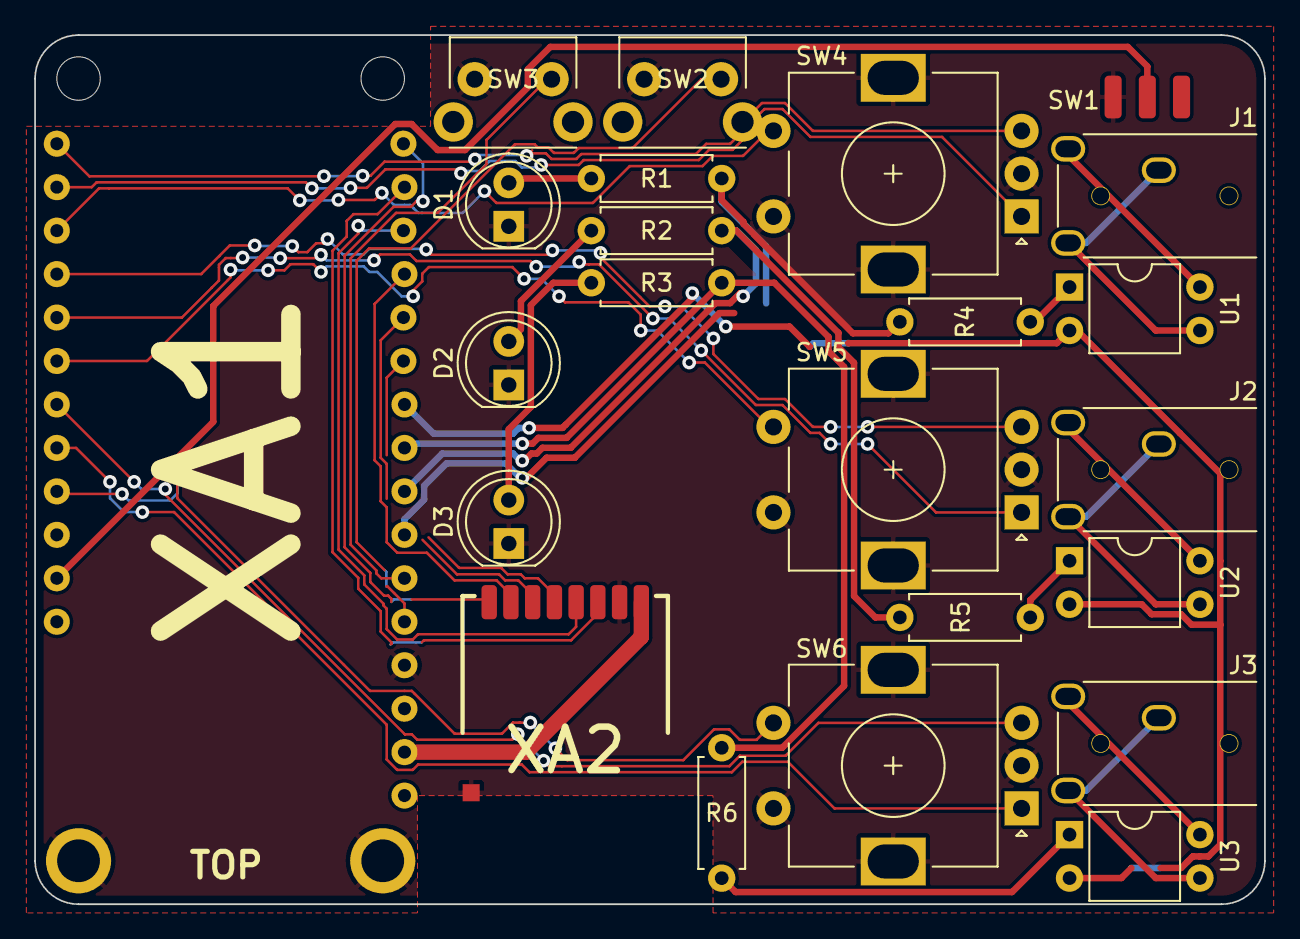
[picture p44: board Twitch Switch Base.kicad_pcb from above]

Board: 2 copper layers, 71.9 x 50.8 mm, 23 parts (0 on the bottom side), 36 nets.

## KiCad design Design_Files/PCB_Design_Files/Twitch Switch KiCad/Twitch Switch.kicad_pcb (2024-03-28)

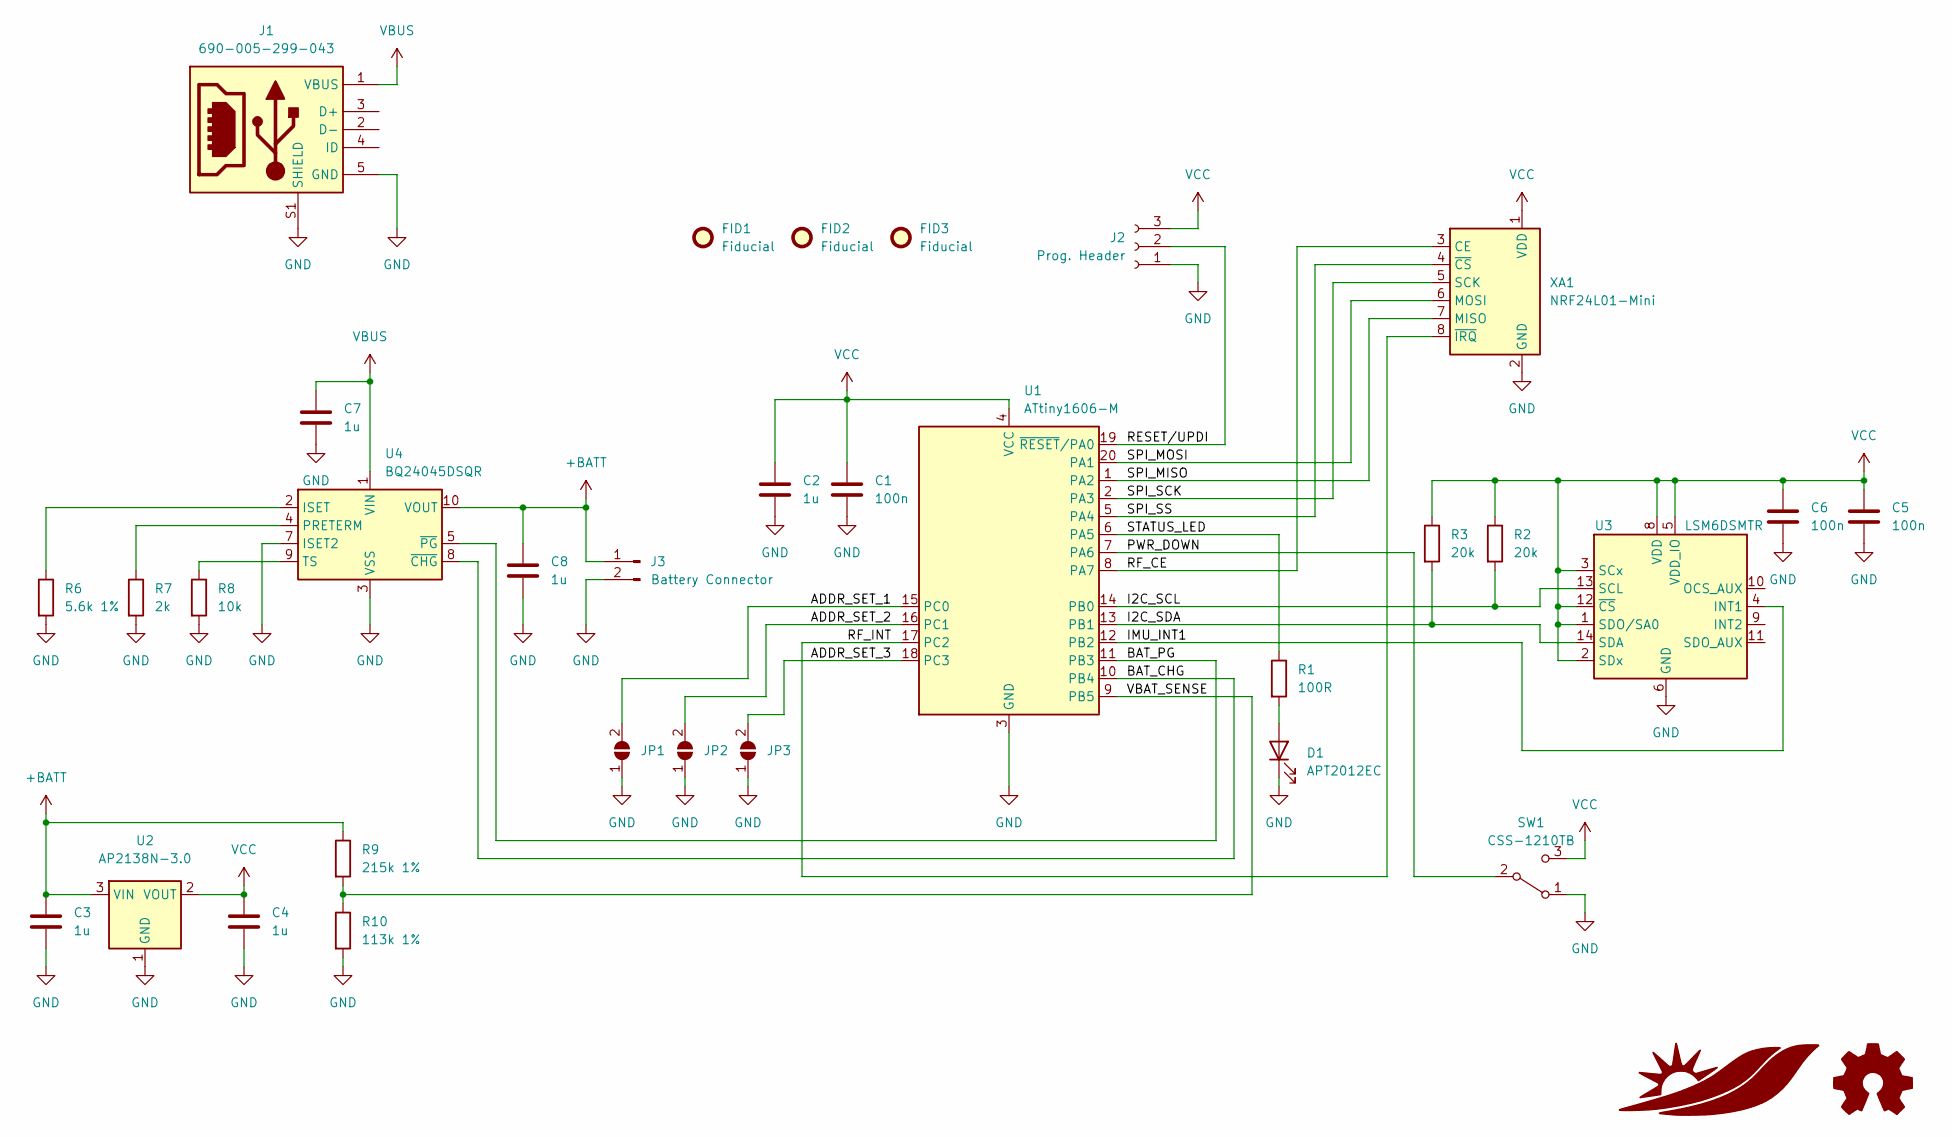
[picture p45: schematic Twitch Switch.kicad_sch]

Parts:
C1: 100n; C_0402_1005Metric; Part CL10B104KB8NNWC
C2, C3, C4, C7, C8: 1u; C_0402_1005Metric; Part CL10B105KP8NFNC
C5, C6: 100n; C_0402_1005Metric; Part CL10B105KP8NFNC
D1: APT2012EC; LED_0805_2012Metric; Part APT2012EC
FID1, FID2, FID3: Fiducial; Fiducial_0.5mm_Mask1mm
J1: 690-005-299-043
J2: Prog. Header; PinHeader_1x03_P2.54mm_Vertical
J3: Battery Connector; JST_PH_S2B-PH-K_1x02_P2.00mm_Horizontal; Part S2B-PH-K-S(LF)(SN)
JP1, JP2, JP3: SolderJumper_2_Open; SolderJumper-2_P1.3mm_Open_RoundedPad1.0x1.5mm
LOGO1: Logo_Open_Hardware_Small; OSHW-Logo_11.4x12mm_SilkScreen
LOGO2: Logo_Stan_Cassidy
R1: 100R; R_0402_1005Metric; Part RMCF0603JT100R
R2, R3: 20k; R_0402_1005Metric; Part RMCF0603JT20K0
R6: 5.6k 1%; R_0402_1005Metric; Part RMCF0603FT5K60
R7: 2k; R_0402_1005Metric; Part RMCF0603JT2K00
R8: 10k; R_0402_1005Metric; Part RMCF0603JT10K0
R9: 215k 1%; R_0402_1005Metric; Part RMCF0603FT215K
R10: 113k 1%; R_0402_1005Metric; Part RMCF0603FT113K
SW1: CSS-1210TB; Part CSS-1210TB
U1: ATtiny1606-M; VQFN-20-1EP_3x3mm_P0.4mm_EP1.7x1.7mm; Part ATtiny1606-MFR
U2: AP2138N-3.0; SOT-23; Part AP2138N-3.0TRG1
U3: LSM6DSMTR
U4: BQ24045DSQR; Part BQ24045DSQR
XA1: NRF24L01-Mini; Part NRF24L01-Mini

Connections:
+BATT: C3.2, C8.2, J3.1, R9.1, U2.3 (VIN), U4.10 (VOUT)
/ADDR_SET_1: JP1.2 (B), U1.15 (PC0)
/ADDR_SET_2: JP2.2 (B), U1.16 (PC1)
/ADDR_SET_3: JP3.2 (B), U1.18 (PC3)
/BAT_CHG: U1.10 (PB4), U4.8 (~CHG)
/BAT_PG: U1.11 (PB3), U4.5 (~PG)
/I2C_SCL: R2.2, U1.14 (PB0), U3.13 (SCL)
/I2C_SDA: R3.2, U1.13 (PB1), U3.14 (SDA)
/IMU_INT1: U1.12 (PB2), U3.4 (INT1)
/PWR_DOWN: SW1.2 (B), U1.7 (PA6)
/RESET/UPDI: J2.2, U1.19 (~RESET/PA0)
/RF_CE: U1.8 (PA7), XA1.3 (CE)
/RF_INT: U1.17 (PC2), XA1.8 (~IRQ)
/SPI_MISO: U1.1 (PA2), XA1.7 (MISO)
/SPI_MOSI: U1.20 (PA1), XA1.6 (MOSI)
/SPI_SCK: U1.2 (PA3), XA1.5 (SCK)
/SPI_SS: U1.5 (PA4), XA1.4 (~CS)
/STATUS_LED: R1.1, U1.6 (PA5)
/VBAT_SENSE: R9.2, R10.1, U1.9 (PB5)
GND: C1.1, C2.1, C3.1, C4.1, C5.1, C6.1, C7.1, C8.1, D1.1 (K), J1.5 (GND), J1.S1 (SHIELD), J1.S2 (SHIELD), J1.S3 (SHIELD), J1.S4 (SHIELD), J2.1, J3.2, JP1.1 (A), JP2.1 (A), JP3.1 (A), R6.2, R7.2, R8.2, R10.2, SW1.1 (A), U1.3 (GND), U1.21 (GND), U2.1 (GND), U3.6 (GND), U3.7 (GND), U4.3 (VSS), U4.7 (ISET2), U4.11 (VSS), XA1.2 (GND), XA1.9 (GND)
unnamed: D1.2 (A), R1.2
unnamed: R6.1, U4.2 (ISET)
unnamed: R7.1, U4.4 (PRETERM)
unnamed: R8.1, U4.9 (TS)
VBUS: C7.2, J1.1 (VBUS), U4.1 (VIN)
VCC: C1.2, C2.2, C4.2, C5.2, C6.2, J2.3, R2.1, R3.1, SW1.3 (C), U1.4 (VCC), U2.2 (VOUT), U3.1 (SDO/SA0), U3.2 (SDx), U3.3 (SCx), U3.5 (VDD_IO), U3.8 (VDD), U3.12 (~CS), XA1.1 (VDD)

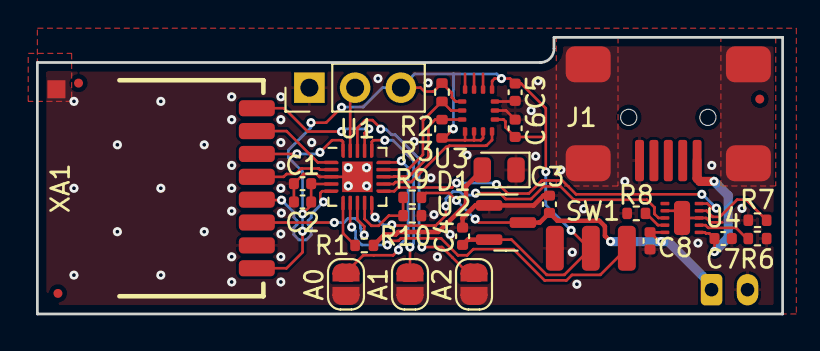
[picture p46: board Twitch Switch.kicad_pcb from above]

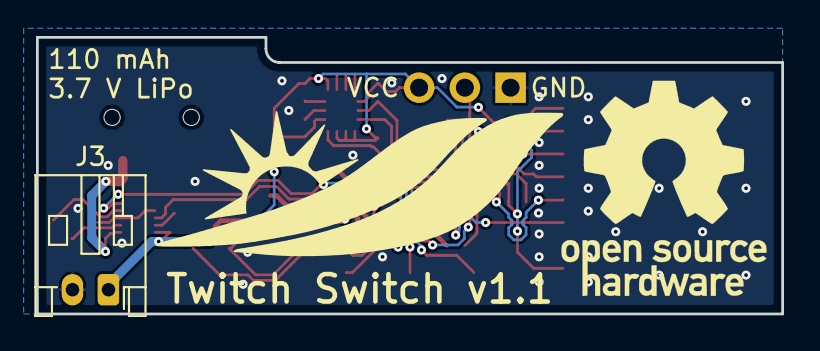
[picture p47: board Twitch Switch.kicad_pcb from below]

Board: 2 copper layers, 41.4 x 15.4 mm, 34 parts (3 on the bottom side), 26 nets.

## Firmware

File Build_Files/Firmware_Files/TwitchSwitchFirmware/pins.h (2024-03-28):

#ifndef __PINS_H__
#define __PINS_H__

// All pins not explicitly defined here are
// taken care of already. This includes I2C and SPI,
// including chip-select.

// Output
#define PIN_STATUS_LED PIN_PA5
#define PIN_RF_CE PIN_PA7

// Input with interrupt on change
#define PIN_PWR_DOWN PIN_PA6

// Input with interrupt on change
#define PIN_IMU_INT1 PIN_PB2
#define PIN_BAT_PG PIN_PB3
#define PIN_BAT_CHG PIN_PB4

// Analog input
#define PIN_VBAT_SENSE PIN_PB5

// Input with interrupt on change
#define PIN_RF_INT PIN_PC2

#endif  /*PINS_H*/

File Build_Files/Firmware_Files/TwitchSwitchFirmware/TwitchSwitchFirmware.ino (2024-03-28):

/*
                   TWITCH SWITCH (SWTICH) Mk-IV

            Stan Cassidy Center for Rehabilitation
                      Oct 25, 2023

            Arduino Platform: 
              Base: Adafruit Feather nRF52840 Express
              SWITCH: CPU - Adafruit ATtiny 1616
                      IMU - https://www.st.com/en/mems-and-sensors/lsm6dsm.html https://www.st.com/resource/en/application_note/an4987-lsm6dsm-alwayson-3d-accelerometer-and-3d-gyroscope-stmicroelectronics.pdf
                      Charger - https://www.ti.com/lit/ds/symlink/bq24045.pdf
            Firmware version number#: TODO: 20231004-01
            For updates, see: https://github.com/rmccaskill/TwitchSwitch2023
            For instructions on building the programmer for the ATTiny, see: https://github.com/SpenceKonde/AVR-Guidance/blob/master/UPDI/jtag2updi.md

            (C)2023 STAN CASSIDY CENTER FOR REHABILITATION (SCCR)
                              ALL RIGHT SRESERVED

                           ===== DISCLAMER =====
  THIS SOFTWARE IS PROVIDED "AS IS", WITHOUT WARRANTY OF ANY KIND, EXPRESS OR
  IMPLIED, INCLUDING BUT NOT LIMITED TO THE WARRANTIES OF MERCHANTABILITY,
  FITNESS FOR A PARTICULAR PURPOSE AND NONINFRINGEMENT. IN NO EVENT SHALL THE
  AUTHORS OR COPYRIGHT HOLDERS BE LIABLE FOR ANY CLAIM, DAMAGES OR OTHER
  LIABILITY, WHETHER IN AN ACTION OF CONTRACT, TORT OR OTHERWISE, ARISING FROM,
  OUT OF, OR IN CONNECTION WITH THE SOFTWARE OR THE USE OR OTHER DEALINGS IN THE
  SOFTWARE.

  ----------------------------------------------------------------------------------------------
TODO: UPDATE

  Special features:
     #Adafruit nRF52840 Feather Express

  Single button operation:
     # Base unit connects to 3 swtiches via radio. These switches stream their data back to the base. The base reads the values 
       and 'decides' when a 'twitch' happens and triggers the appropriate action (move move / button press)
     # Three profiles - indivudually tuned for different scenarios. For example: sitting in a chair vs laying in bed.

  LED messages:
    NOTE - CHARGE INDICATORS AREN'T WORKING YET
  //Battery State indicator (TODO)
  // Low battery = Power ON:  Blink LED every few seconds
  // Charging = POWER ON or OFF: Breath LED
  // Charged = POWER ON or OFF: LED ON SOLID

  NOTES
  - For programming the firmware - see https://github.com/SpenceKonde/AVR-Guidance/blob/master/UPDI/jtag2updi.md
*/

#include <SPI.h>
#include <RF24.h>
#include <nRF24L01.h>

#include "pins.h"
#include <avr/sleep.h>

#include <stdio.h>

#include <Wire.h>
#include "lsm6dsm.h"

#define WM_LEVEL 192
#define WU_THRESHOLD 2

RF24 radio(PIN_RF_CE, PIN_SPI_SS);
lsm6dsm imu;

uint8_t readbuf[32];
uint8_t buffer[24];

uint8_t ourAddress[5] = { 0x8d, 0x97, 0xb0, 0xe7, 0x47 };

// Semiphore to track when power switch has changed state
volatile uint8_t handlePowerSwitch = 1; //On first - we want the LED to blink if it's plugged in and turned on.

volatile uint8_t handleIMUInterrupt = 0;
volatile uint8_t handleRadioInterrupt = 0;


//Charger details: https://www.ti.com/lit/ds/symlink/bq24045.pdf?ts=1706249391058
volatile uint8_t handleBatPG = 0; //Low (FET on) indicates the input voltage is above UVLO and the OUT (battery) voltage.
volatile uint8_t handleBatCharge = 0; //Low (FET on) indicates charging and Open Drain (FET off) indicates no Charging or Charge complete
volatile uint8_t handleBatSense = 0; // What does this do?

//Power states: ON, Charging, Charged, OFF

enum {
  MODE_OFF = 0,
  MODE_WAITING = 1,
  MODE_SENDING = 2,
};

uint8_t mode = MODE_OFF;

ISR(PORTC_PORT_vect, ISR_ALIASOF(PORTA_PORT_vect));
ISR(PORTB_PORT_vect, ISR_ALIASOF(PORTA_PORT_vect));
ISR(PORTA_PORT_vect) {
  // 1 - why are we here. Who fired?
  // 2 - Respond to the cause
  // 3 - clear interrupt flag
  byte flags_a = VPORTA.INTFLAGS;
  byte flags_b = VPORTB.INTFLAGS;
  byte flags_c = VPORTC.INTFLAGS;

  // 1st - check if it was the power switch
  // Power is on PORTA PA6, so check there
  if (flags_a & (1 << 6)) {
    handlePowerSwitch = 1;
    VPORTA.INTFLAGS |= (1 << 6);
  }

  // 1st - check if it was the IMU that interrupted
  // IMU_INT1 is on PB2, so check there
  if (flags_b & (1 << 2)) {
    handleIMUInterrupt = 1;
    VPORTB.INTFLAGS |= (1 << 2);
  }

  // BAT_PG is on PB3
  if (flags_b & (1 << 3)) {
    handleBatPG = 1;
    VPORTB.INTFLAGS |= (1 << 3);
  }

  // BAT_CHG is on PB4
  if (flags_b & (1 << 4)) {
    handleBatCharge = 1;
    VPORTB.INTFLAGS |= (1 << 4);
  }

  // PIN_VBAT_SENSE is on PB5
  if (flags_b & (1 << 5)) {
    handleBatSense = 1;
    VPORTB.INTFLAGS |= (1 << 5);
  }
  

  // RADIO_INT is on PC2
  if (flags_c & (1 << 2)) {
    handleRadioInterrupt = 1;
    VPORTC.INTFLAGS |= (1 << 2);
  }
}

/*
ISR(TCA0_CMP0_vect) {
  // LED alarm tripped
  TCA0.SINGLE.INTFLAGS = TCA_SINGLE_CMP0_bm;
  // Do the stuff to handle the LED

  // If we want to turn LED on in 5.76 seconds:
  // Multiply seconds by clock rate - 5.76 * 5e6 / 64 = 450000
  // Take cycle number and divide by 2^16 for number of overflows required: 450000 / 2^16 = 6
  // Take remainder of previous division and multiply by 2^16 for the alarm compare: 0.86645508*2^16 = 56784

  TCA0.SINGLE.CMP0 = TCA0.SINGLE.CNT + 39062;
  digitalWriteFast(PIN_STATUS_LED, !digitalReadFast(PIN_STATUS_LED));
}
*/

void handleWDR() {
  // Copy all important bug-detection info somewhere safe. We want to look at it to diagnose the problem.
}

/*
void init_TCA0() {
  TCA0.SINGLE.PER = 0xFFFF;  // This can be changed. Currently as high as possible
  TCA0.SINGLE.CTRLB = TCA_SINGLE_WGMODE_SINGLESLOPE_gc;
  TCA0.SINGLE.INTCTRL = TCA_SINGLE_CMP0_bm;  // Enable LED interrupt
  TCA0.SINGLE.CTRLA = (TCA_SINGLE_CLKSEL_DIV64_gc | TCA_SINGLE_ENABLE_bm);
}
*/

void setup() {
  // If WDT caused reset, run handleWDR.
  uint8_t resetcause = GPIOR0;
  if (resetcause & 0x08) {
    handleWDR();
  }

  set_sleep_mode(SLEEP_MODE_IDLE); // Use standby for 100x less power, but only if you don't need TCA0
  sleep_enable();

  pinConfigure(PIN_STATUS_LED, OUTPUT);
  //For more details about configuring pins on the ATtiny - sell https://github.com/SpenceKonde/megaTinyCore/blob/master/megaavr/extras/Ref_Digital.md

  //Configure the pins so that we can read which switch this is (1,2,3)
  pinConfigure(PIN_PC0, PIN_PULLUP | PIN_DIR_INPUT);
  pinConfigure(PIN_PC1, PIN_PULLUP | PIN_DIR_INPUT);
  pinConfigure(PIN_PC3, PIN_PULLUP | PIN_DIR_INPUT);

  pinConfigure(PIN_IMU_INT1, PIN_DIR_INPUT | PIN_ISC_RISE);
  pinConfigure(PIN_PWR_DOWN, PIN_DIR_INPUT | PIN_ISC_CHANGE);


  pinConfigure(PIN_BAT_PG, PIN_DIR_INPUT | PIN_ISC_CHANGE);
  pinConfigure(PIN_BAT_CHG, PIN_DIR_INPUT | PIN_ISC_CHANGE);
  pinConfigure(PIN_VBAT_SENSE, PIN_DIR_INPUT | PIN_ISC_CHANGE);

  delay(15);

  Wire.begin();
  Wire.setClock(400000);

  //Read in port C. Mask off the blobs that we're interested in. These are the solder blobs on the board. A0, A1, A2 on the board
  uint8_t configPins = VPORTC.IN & 0b00001011;
  ourAddress[0] += configPins;  //Added to 0x8d

  // We can save some power by turning off the pads we read as grounded (soldered)
  if (!(configPins & (1 << 3))) {
    // PC3 IS soldered
    pinConfigure(PIN_PC3, PIN_DIR_INPUT);
  }
  if (!(configPins & (1 << 1))) {
    // PC1 IS soldered
    pinConfigure(PIN_PC1, PIN_DIR_INPUT);
  }
  if (!(configPins & (1 << 0))) {
    // PC0 IS soldered
    pinConfigure(PIN_PC0, PIN_DIR_INPUT);
  }
  //1010, 1001, 0011

  //Initial mode (on / off) based on the power switch
  if (digitalReadFast(PIN_PWR_DOWN) == 1) {
    //ON
    mode = MODE_WAITING; 
  }
  else
  {
    mode = MODE_OFF; 
  }
  

  while (!radio.begin())
    ;

  radio.setDataRate(RF24_2MBPS);
  radio.enableDynamicPayloads();
  //radio.enableAckPayload();
  
  //Nov 18
  radio.setAutoAck(false);

  radio.setPALevel(0);
  radio.setChannel(57);
  radio.openWritingPipe(ourAddress);
  radio.stopListening();
}

bool isCharging = false; //digitalReadFast(PIN_BAT_CHG);

void startCharging()
{
  digitalWriteFast(PIN_STATUS_LED, HIGH);
  isCharging = true;
}

void stopCharging()
{
  digitalWriteFast(PIN_STATUS_LED, LOW);
  isCharging = false;
}

void blinkLED(long msDelay)
{
  for (uint8_t i = 0; i < 10; i++) {
    digitalWriteFast(PIN_STATUS_LED, !digitalReadFast(PIN_STATUS_LED));
    delay(msDelay);
  }
  digitalWriteFast(PIN_STATUS_LED, LOW);
}

// Note - this is blocking. Don't use in production. Debugging only.
void breathLED()
{
  for (uint8_t i = 0; i < 255; i++) {
    analogWrite(PIN_STATUS_LED, i);
    delay(5);
  }

  for (uint8_t i = 255; i > 0; i--) {
    analogWrite(PIN_STATUS_LED, i);
    delay(5);
  }
  digitalWriteFast(PIN_STATUS_LED, LOW);

}

void loop()
{

/*
  // Note Feb 2, 2024.PIN_BAT_CHG NOT high when charging. PIN_BAT_CHG is seemingly NEVER high...
  // From DOCS: CHG 8 8 O Low (FET on) indicates charging and Open Drain (FET off) indicates no Charging or Charge complete
  if (digitalReadFast(PIN_BAT_PG) == LOW)
  {
    digitalWriteFast(PIN_STATUS_LED, HIGH);
    //startCharging();
  }
  else
  {
    digitalWriteFast(PIN_STATUS_LED, LOW);
    //stopCharging();

  }
  //return; 
*/
  static uint8_t packetnum = 0;


  //Read vbat somehow? See https://forum.arduino.cc/t/voltage-reading/57530/2
  //r9 = 215k ohm
  //r10 = 113k ohm
  //const float R9 = 215000.0; // Put exact value here
  //const float R10 = 113000.0; // Put exact value here
  //const float Vref = 3.7;   // Put exact value here
  //int adcReading = analogRead(PIN_VBAT_SENSE);
  //float voltage = (R9+R10)/R9 * adcReading * Vref / 1024.0;

/*
  if (handleBatCharge)
  {
    cli();  // Disable interrupts
    handleBatCharge = 0;
    sei();  // Enable interrupts

    if (digitalReadFast(PIN_BAT_CHG))
      startCharging();
    else
      stopCharging();
  }
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

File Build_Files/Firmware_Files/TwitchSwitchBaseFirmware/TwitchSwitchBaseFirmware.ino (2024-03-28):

/*
                   TWITCH SWITCH (BASE UNIT) Mk-IV

            Stan Cassidy Center for Rehabilitation
                      Feb 23, 2023

            Arduino Platform: 
              Base: Adafruit Feather nRF52840 Express

            Firmware version number#: 20231220 v1.1

            (C)2023 STAN CASSIDY CENTER FOR REHABILITATION (SCCR)
                              ALL RIGHT SRESERVED

                           ===== DISCLAMER =====
  THIS SOFTWARE IS PROVIDED "AS IS", WITHOUT WARRANTY OF ANY KIND, EXPRESS OR
  IMPLIED, INCLUDING BUT NOT LIMITED TO THE WARRANTIES OF MERCHANTABILITY,
  FITNESS FOR A PARTICULAR PURPOSE AND NONINFRINGEMENT. IN NO EVENT SHALL THE
  AUTHORS OR COPYRIGHT HOLDERS BE LIABLE FOR ANY CLAIM, DAMAGES OR OTHER
  LIABILITY, WHETHER IN AN ACTION OF CONTRACT, TORT OR OTHERWISE, ARISING FROM,
  OUT OF, OR IN CONNECTION WITH THE SOFTWARE OR THE USE OR OTHER DEALINGS IN THE
  SOFTWARE.

  ----------------------------------------------------------------------------------------------
TODO: UPDATE

  Special features:
     #Adafruit nRF52840 Feather Express

  Single button operation:
     # Base unit connects to 3 swtiches via radio. These switches stream their data back to the base. The base reads the values 
       and 'decides' when a 'twitch' happens and triggers the appropriate action (move move / button press)
     # Three profiles - indivudually tuned for different scenarios. For example: sitting in a chair vs laying in bed.

  Visual of the board for referance

       |
  -O  [‾]      KNOB 3, SWITCH [2], SENSOR 1
  -O  [ ]      KNOB 2, SWITCH [1], SENSOR 2
  -O  [_]      KNOB 1, SWITCH [0], SENSOR 3

  LED messages:
    - Need to decide on 'charging indicators'
*/

#include <SPI.h>
#include <RF24.h>
#include <nRF24L01.h>
#include <Adafruit_NeoPixel.h>

#include <Adafruit_TinyUSB.h>

#include <bluefruit.h>

// Set up file system for storage
#include <Adafruit_LittleFS.h>  //https://github.com/adafruit/Adafruit_nRF52_Arduino/tree/master/libraries/Adafruit_LittleFS
#include <InternalFileSystem.h>
using namespace Adafruit_LittleFS_Namespace;
#define FILENAME "/twitchswitch.txt"
File file(InternalFS);

#include <SwRotaryEncoder.h>

#include <AceButton.h>  // See https://github.com/bxparks/AceButton#Features
using namespace ace_button;

#include "pins.h"

BLEDis bledis;          //Bluetooth Device Information Service  https://learn.adafruit.com/introducing-the-adafruit-nrf52840-feather/bledis
BLEHidAdafruit blehid;  //BLEHidAdafruit allows you to simulate a mouse or keyboard using the HID (Human Interface Device) profile that is part of the Bluetooth Low Energy standard.

SwRotaryEncoder knobs[3];

RF24 radio(PIN_RADIO_CE, PIN_RADIO_CS, 10000000UL);

Adafruit_NeoPixel pixel(1, PIN_NEOPIXEL, NEO_GRB + NEO_KHZ800);

//Radio pipe Config
uint8_t switch1_pipe[5] = { 0x97, 0x97, 0xb0, 0xe7, 0x47 };
uint8_t switch2_pipe[5] = { 0x96, 0x97, 0xb0, 0xe7, 0x47 };
uint8_t switch3_pipe[5] = { 0x90, 0x97, 0xb0, 0xe7, 0x47 };

uint8_t readbuf[32];

#define PULSE_LEN 250     // Output pulse duration in milliseconds

#define BAUD_RATE 115200  // USB communications baud rate
#define VERSION_TWITCHSWITCH "1.2" //1.2 added battery improvements and keyboard mode

// Constants for OPERATION MODES
const uint8_t MODE_MOUSE = 0; //GREEN
const uint8_t MODE_TABLET = 1; //BLUE
const uint8_t MODE_KEYBOARD = 2; //YELLOW
const uint8_t MODE_AIRMOUSE = 3; //ORANGE?


// Constants for HOW THE MOUSE POINTER IS MOVING
const uint8_t MOUSE_STOPPED = 0;
const uint8_t MOUSE_MOVING_UP = 1;
const uint8_t MOUSE_MOVING_DOWN = 2;
const uint8_t MOUSE_MOVING_RIGHT = 3;
const uint8_t MOUSE_MOVING_LEFT = 4;

// Constants for WHICH SENSOR WAS TRIGGERED (same as the numbers on the sensor case)
const uint8_t SENSOR_CLICK = 1;
const uint8_t SENSOR_LEFTRIGHT = 2;
const uint8_t SENSOR_UPDOWN = 3;

uint8_t currentMouseMode = MOUSE_STOPPED;

// Accelleration settings
uint32_t mouseMoveStartTime = 0;  //When the mouse STARTED moving (so we can try some accelleration of some kind)
uint8_t mouseBaseSpeed = 1;
uint8_t maxAccelleration = 4; // This will cause the mouse speed to start at 1, then change to 2, then change to 4 each time it starts moving

uint32_t lastWatermarkupdate = 0;  //When the last time a rotary encoder was changed

//************ BUTTON CONFIG ************
// Create 2 ButtonConfigs. The System ButtonConfig is not used.
ButtonConfig modeConfig;
ButtonConfig profileConfig;
ButtonConfig knobButtonsConfig;
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

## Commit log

2024-11-06 Version 3.1 - Updated Sensor Programmer
    Sensor programmer - wiring has been updated, resistor removed, and changed the diode. Maker Guide and BOM have been updated to reflect these changes. Typo in Maker Guide fixed.
    [Twitch_Switch_BOM.csv, Twitch_Switch_BOM.xlsx]
2026-02-10 Update TS_Controller_Fabrication.zip
    Fixed tactile switch hole location
